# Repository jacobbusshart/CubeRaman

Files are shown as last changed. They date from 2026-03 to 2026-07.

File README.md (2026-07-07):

# CubeRaman

*3D-Printed Raman Spectrometer*

This project aims to make Raman spectroscopy more accessible, replicable and - in the first place - affordable. It can be used to non-destructively identify chemicals, polymers, pharmaceuticals and minerals in an experimental setting.

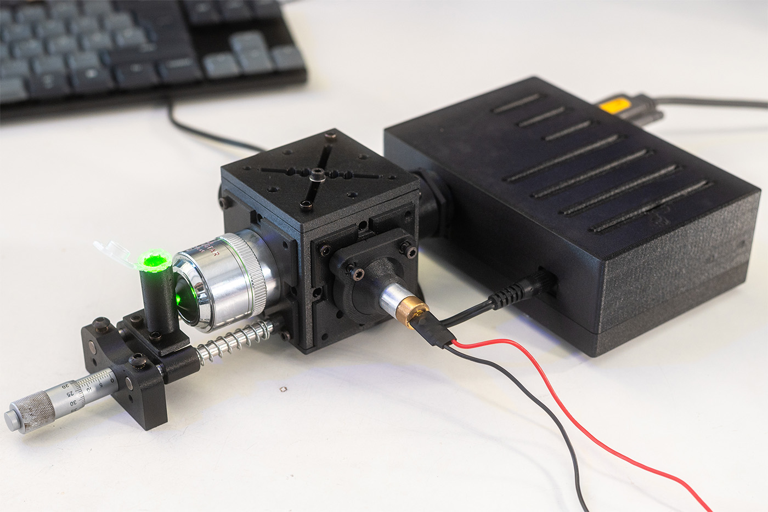
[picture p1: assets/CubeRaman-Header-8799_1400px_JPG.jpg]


It is designed in a back-scattering configuration - both exciting and collecting through the microscope objective. It uses a 532nm laser at ~30mW, utilizing filters with a cut-on at 550nm, which effectively allows for Raman measurements in the wavenumber range of 600cm<sup>-1</sup>- 3000cm<sup>-1</sup>

> ⚠ **This build uses a Class 3B laser. Certified laser safety glasses rated for 532nm are mandatory** — see the note in [Sourced Parts](#sourced-parts). Keep the laser disconnected during assembly and never look into the beam path or the objective, even with protection on. Remove watches and rings while aligning - stray reflections mostly come as a surprise. Know your local regulations for Class 3B laser operation.

**Contents:** [Sample Spectra](#sample-spectra) · [How It Works](#how-it-works) · [3D-Model](#3d-model) · [Sourced Parts](#sourced-parts) · [3D-Printed Parts](#3d-printed-parts) · [Instructions](#instructions) · [Calibration, Alignment & First Light](#calibration-alignment--first-light) · [Software](#software) · [Build Video](#build-video) · [Various](#various)

---
## Sample Spectra
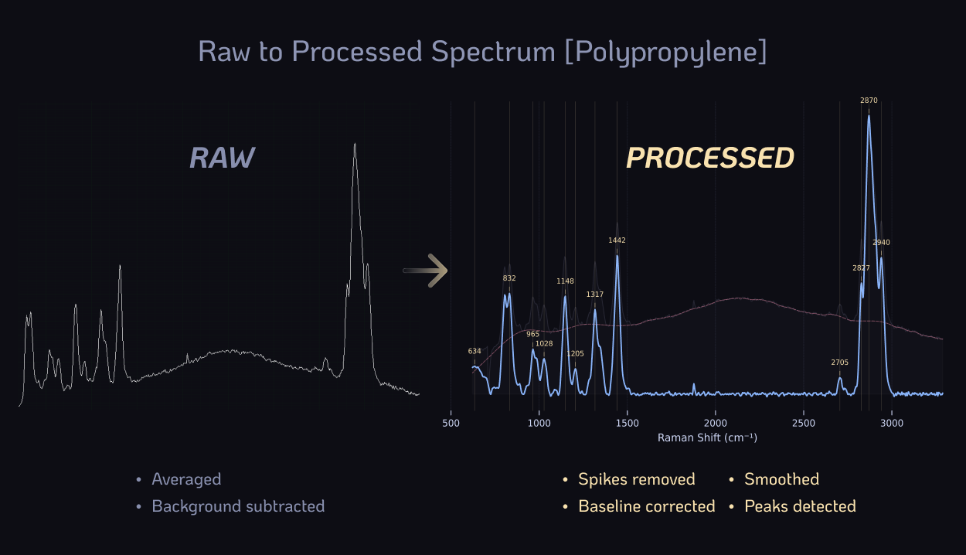
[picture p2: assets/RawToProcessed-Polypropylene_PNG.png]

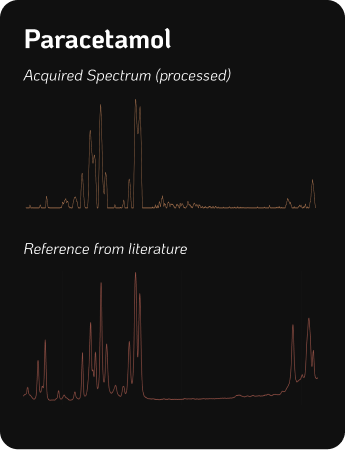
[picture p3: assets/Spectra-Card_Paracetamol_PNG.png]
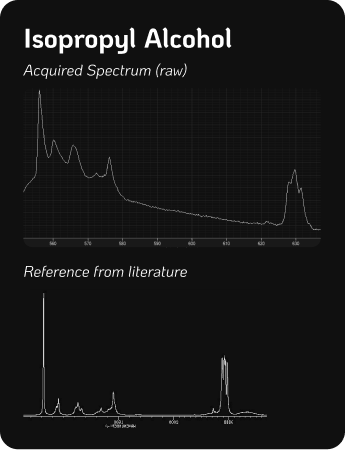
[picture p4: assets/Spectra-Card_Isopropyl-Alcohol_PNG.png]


Verified so far: **polypropylene/-ethylene, paracetamol, isopropyl alcohol, ethanol, diamond, beta-carotene and more.**

Examples of the expected spectral performance. The resolution - how narrow or wide a peak is and thus their separability - is determined by a multitude of factors. With the main bottleneck of the system being the 100 micron input slit of the spectrometer unit. The beam diameter is also a factor, along with its stability and IR-leakage. A higher resolution spectrometer will definitely yield significantly better results - though at a significant cost.

---

## How It Works

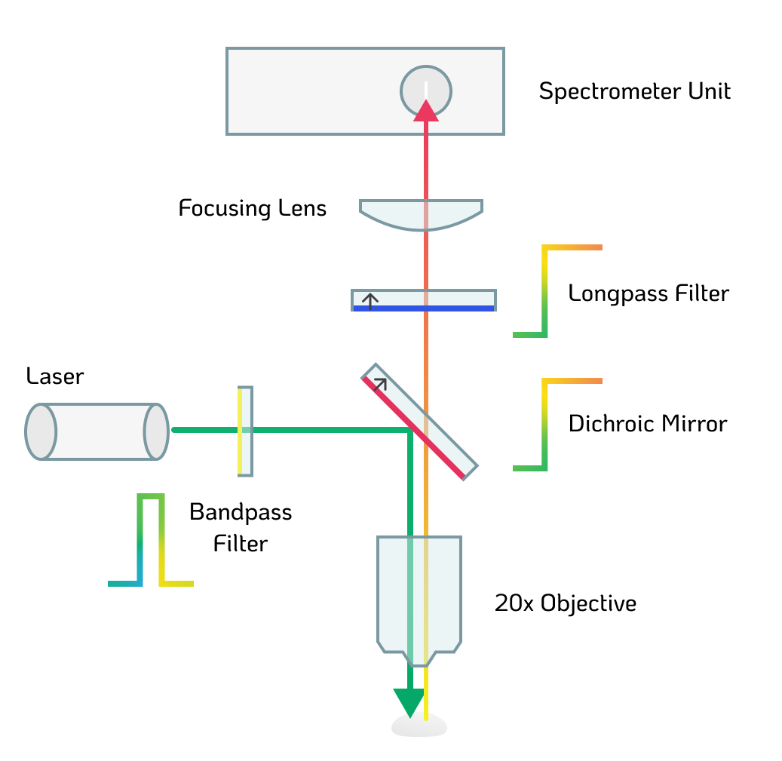
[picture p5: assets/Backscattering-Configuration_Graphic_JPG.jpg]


The **532 nm laser** fires horizontally. The **bandpass filter** strips IR leakage from the cheap diode module and narrows the laser's wavelength. The beam then hits the **DMLP550 dichroic mirror** at 45°, which reflects it 90° downward through the **20x objective** and onto the **sample**.
Backscattered light travels back up through the objective. The Raman-shifted photons (>550 nm) transmit straight through the dichroic toward the detector, while the unwanted Rayleigh-scattered 532 nm light passes into the beam dump. The **FELH0550 longpass filter** gives a second stage of Rayleigh rejection, the **f=19mm achromat** focuses the beam onto the 100 μm slit, and the **B&W Tek spectrometer** records the spectrum.

The acquired spectrum is processed to remove residual background or fluorescence interference and make it more legible. That means: cropping and calculating Raman-shift, cosmic spike removal, baseline correction, smoothing and normalizing. Additionally, peaks can be detected and fitted, though this is more relevant for high-performance/-resolution Raman instruments that have been calibrated to certified standards. See [Software](#software) for the included processing tool.

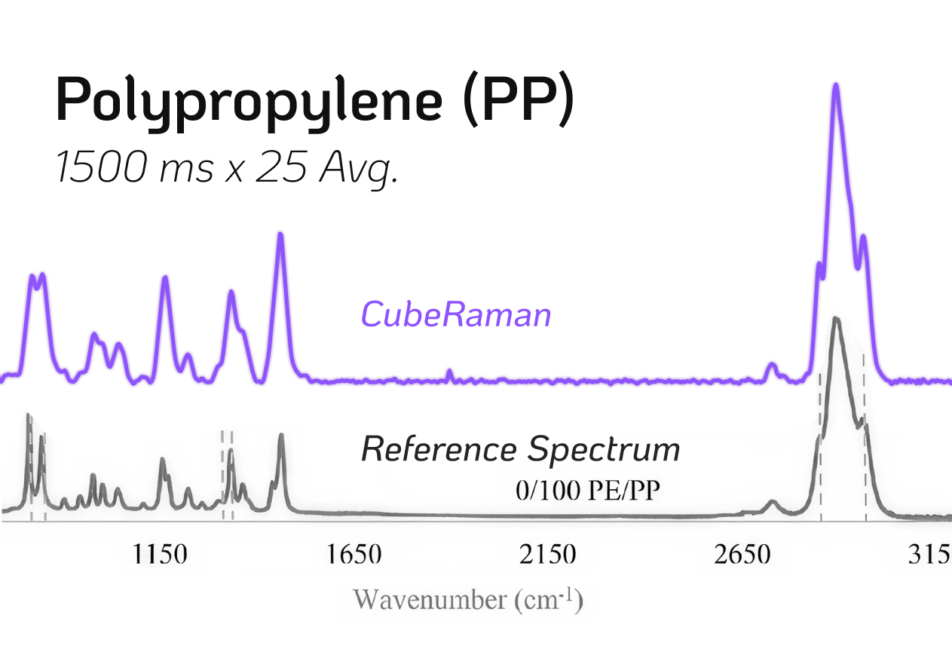
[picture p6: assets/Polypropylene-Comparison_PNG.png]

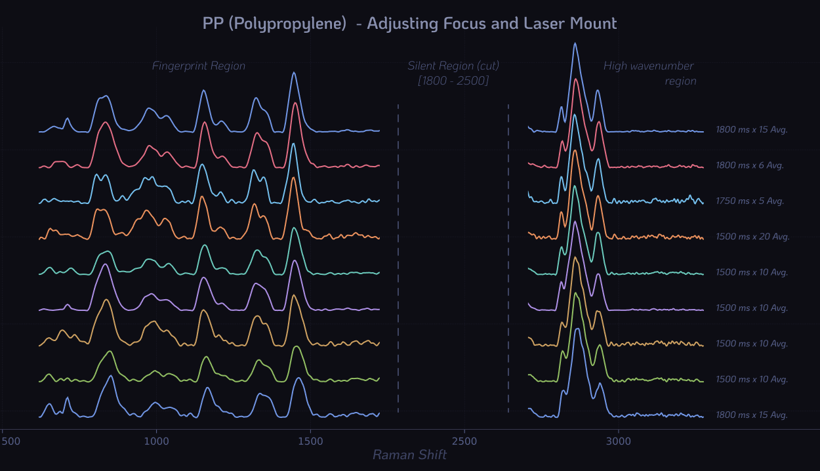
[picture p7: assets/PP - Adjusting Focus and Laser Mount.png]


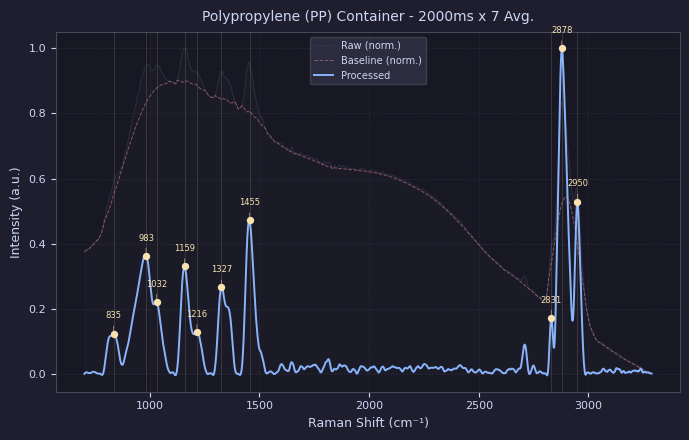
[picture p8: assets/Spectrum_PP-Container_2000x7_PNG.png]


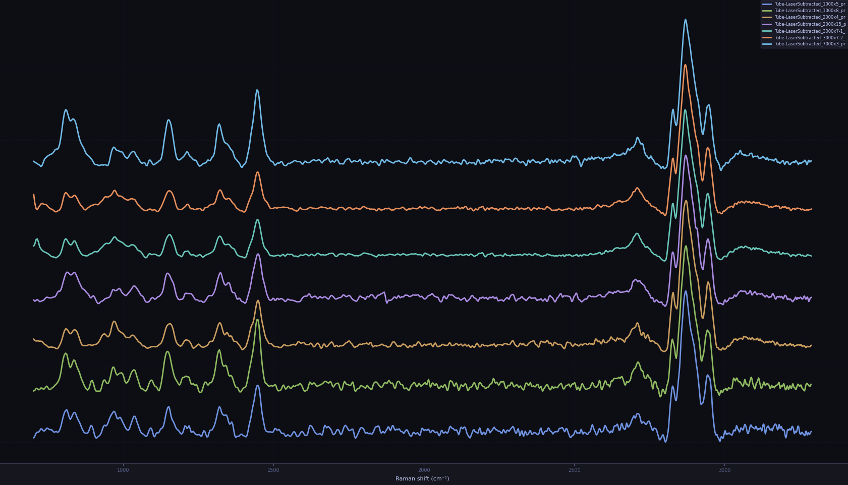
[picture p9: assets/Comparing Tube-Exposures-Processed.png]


--- 

## 3D-Model

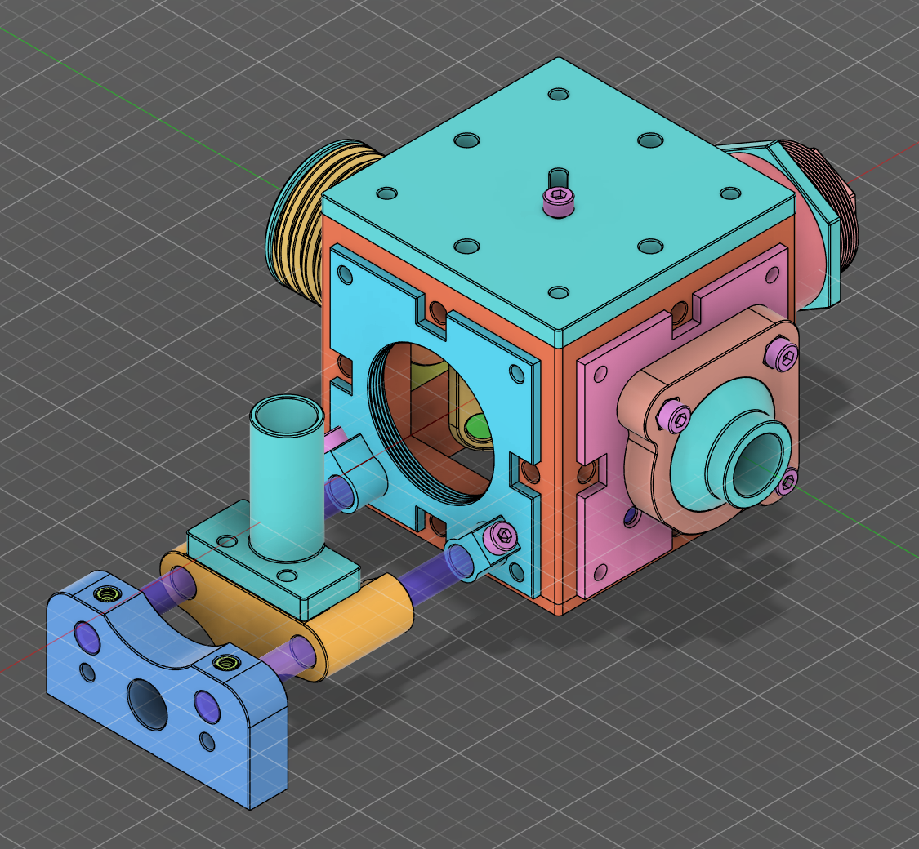
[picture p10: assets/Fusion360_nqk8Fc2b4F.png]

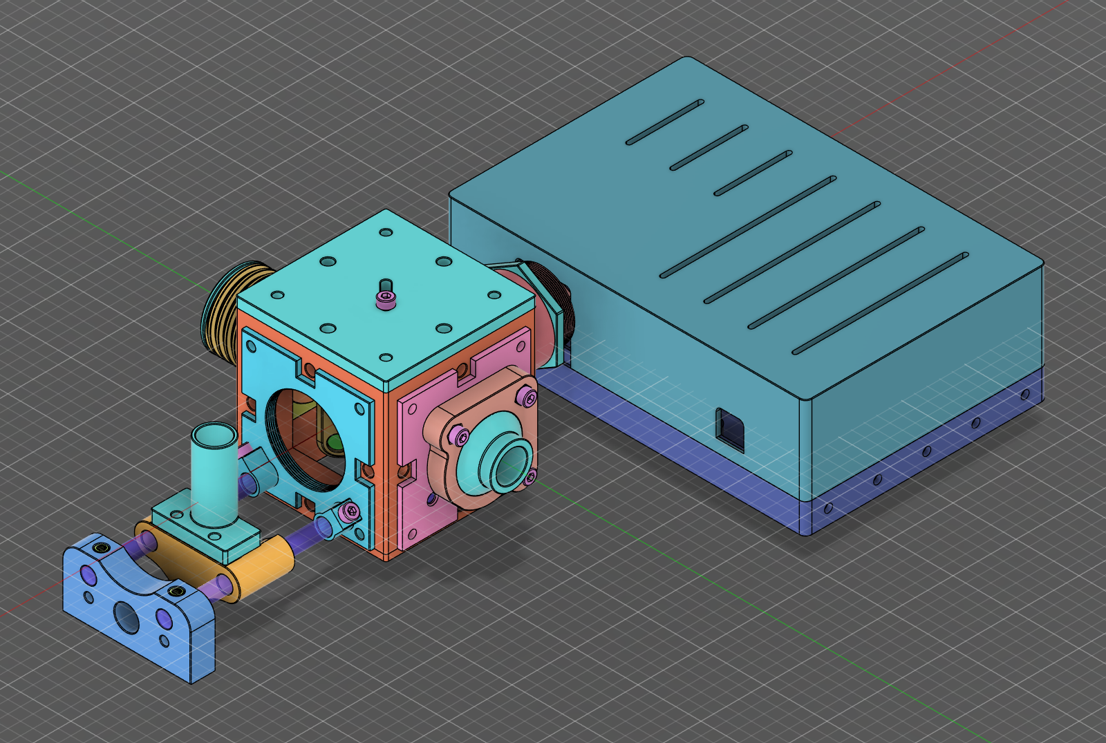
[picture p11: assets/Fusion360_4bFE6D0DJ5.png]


A more detailed overview of the printed parts are depicted in the section below.

---

## Sourced Parts

| Part                                                                                       | Description / Specification                                                                                                                            | Cost                          |
| ------------------------------------------------------------------------------------------ | ------------------------------------------------------------------------------------------------------------------------------------------------------ | ----------------------------- |
| [DMLP550](https://www.thorlabs.com/item/DMLP550)                                           | Ø1" Longpass Dichroic Mirror, 550nm Cut-On                                                                                                             | <p align="right">195€</p>     |
| [FELH0550](https://www.thorlabs.com/item/FELH0550)                                         | Ø25.0mm Longpass Filter, 550nm Cut-On<br>(or the new 1/2" version FELH05550)                                                                           | <p align="right">150€</p>     |
| [#65640](https://www.edmundoptics.com/p/532nm-cwl-10nm-fwhm-125mm-mounted-diameter/20158/) | Bandpass Filter 532nm, 10nm FWHM                                                                                                                       | <p align="right">95€</p>      |
| [AC127-019-A](https://www.thorlabs.com/item/AC127-019-A)                                   | Ø1/2" Achromatic Doublet, f=19mm                                                                                                                       | <p align="right">59€</p>      |
| Microscope Objective                                                                       | Any used/new, infinity-corrected, 20x                                                                                                                  | <p align="right">50€</p>      |
| [B&W Tek BTC 100-2S](https://ebay.us/m/y6hDoC)                                             | Surplus spectrometer unit, 100μm slit, 450-650nm                                                                                                       | <p align="right">180€</p>     |
|                                                                                            | + Any [5V / 2A+ DC Power Supply](https://amzn.eu/d/00yvyamx) (Barrel Jack)<br>+ Any [RS232-to-USB Cable](https://amzn.eu/d/01SqgRPR) for Communication |                               |
| [532nm Laser Pointer](https://aliexpress.com/item/1005004415839015.html)                   | Any (cheap) 532nm laser module, >30mW, (Ø12mm)                                                                                                         | <p align="right">10€</p>      |
| + Various                                                                                  | M3 Screws + Nuts, M3 Heat Set Inserts, <br>Magnets 6x2mm                                                                                               | <p align="right">10€</p>      |
| [Optional](https://aliexpress.com/item/1005008245139319.html)                              | Any Fiber Optic Cable, SMA905, +-200μm core                                                                                                            | <p align="right">(50€)</p>    |
|                                                                                            | <p align="right">**TOTAL**</p>                                                                                                                         | <p align="right">**749€**</p> |

**<u>High-quality laser safety glasses are mandatory to protect your eyes from the powerful laser and its reflections!</u>** Buy a certified pair from a reputable supplier, not Aliexpress! They should be rated for the laser's wavelength at 532nm. I bought [these](https://protect-laserschutz.de/de/shop/~p1924) from a local German brand for around 130€.

Notes on the two "wildcard" parts:
- **Spectrometer**: the BTC 100-2S is the cost compromise of this build - its 100μm slit is the main resolution bottleneck. Any spectrometer covering roughly 550-650nm will work; a better one yields sharper peaks, though often at significant cost.
- **Microscope Objective**: must be **infinity-corrected** - the design places the dichroic and longpass filter in collimated space and uses the achromat as the tube lens. A finite (160mm) objective will not work without redesign! Also keep in mind that anything >20x often features a working distance too short for measuring inside containers or a cuvette (though at higher NA = more signal). 20x is the best compromise, from my experience at least.

---
## 3D-Printed Parts

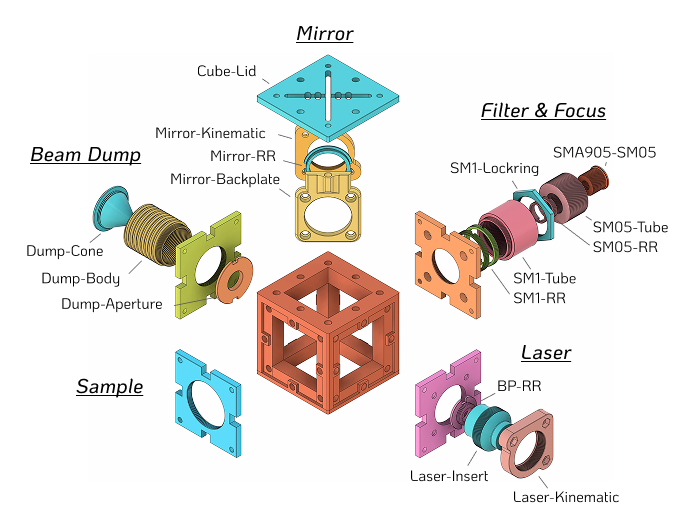
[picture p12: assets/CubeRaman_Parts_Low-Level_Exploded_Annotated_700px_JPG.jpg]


### Base Cube & Sides

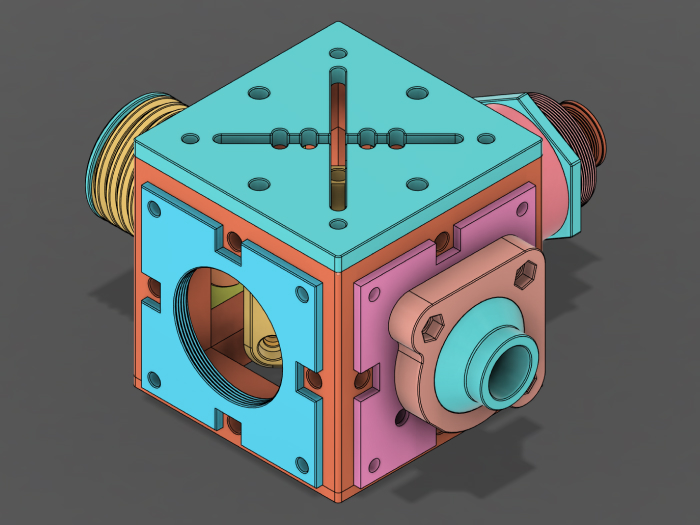
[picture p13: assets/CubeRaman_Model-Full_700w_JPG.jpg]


Print the base cube along with the side plates first. Afterwards print the rest of the grouped parts below.

All parts were printed without supports and are only printed once!

| Base Cube + Sides       |
| ----------------------- |
| Base-Cube               |
| Base-Cube-Top           |
| Cube-Insert_Sample      |
| Cube-Insert_Dump        |
| Cube-Insert_Laser       |
| Cube-Insert_FilterFocus |

### Parts

| **Laser**       | **Mirror**       | **Filter & Focus** | **Beam Dump** | **Sample** |
| --------------- | ---------------- | ------------------ | ------------- | ---------- |
| Laser-Insert    | Mirror-Kinematic | SM1-Tube           | Dump-Body     | -          |
| Laser-Kinematic | Mirror-Backplate | SM05-Tube          | Dump-Cone     |            |
| BP-RR           | Cube-Lid         | SM1-Lockring       | Dump-Aperture |            |
|                 | Mirror-RR        | SMA905-SM05        |               |            |
|                 |                  | SM1-RR (2x)        |               |            |
|                 |                  | SM05-RR (2x)       |               |            |

| **Extras**     |
| -------------- |
| Spanner_SM1RR  |
| Spanner_SM05RR |

Printed on a Bambu P1S using high resolution exports out of Fusion and sliced using BambuStudio

- PETG-CF (Black) 
- 0.4mm Hardened Steel Nozzle
- 0.12mm Layer height
- 4 Walls, 50% Gyroid infill
- Seam position Nearest or Random
- Precision parameters set to 0.001mm

---
## Instructions

*Full step-by-step version: [Hackaday.io Instructions](https://hackaday.io/project/205344/instructions)*

- I use a Bambu P1S with a 0.4mm hardened steel nozzle and extruder
- Filament is ideally non-reflective and dark / black to reduce stray light; I used black PETG-CF as it's my favorite and matte. The stiffer the better; PLA-CF is also a sensible alternative. 
### 1. Printing

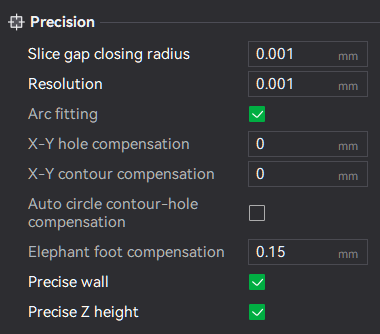
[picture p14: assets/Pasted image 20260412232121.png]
- Set "**Precision**" settings in your slicer (*may just be placebo*) 
- **No Supports** are needed for any of the parts!
- **Print Orientation**: face flat / perpendicular to the build plate - especially for threads, which must be printed vertically for clean engagement! "**Auto-Orient**" should always do the trick.
- **Layer Height** set to at least **0.12mm**. (at least for the parts with threads or fine features) 
- "**Seam Position**" is set to **Nearest** or Random for a better fit.

- All parts should be easy to print; the Base-Cube being the most demanding, as it features overhangs. (TO BE REVISED to 45° to facilitate printing)
- For the **Cube-Inserts** and the **Cube-Lid** especially, it is best to let the build plate / part cool down before removing it. This is good practice to avoid bending the part and introducing permanent deformation.
- Also print the two spanner tools (**Spanner_SM1RR**, **Spanner_SM05RR**) - they make tightening the retaining rings much easier later.

### 2. Assembly

#### Base-Cube

**Printed Parts:** Base-Cube, Base-Cube-Top
**Sourced Parts:** (24x) M3 Heat Set Inserts (Length: 4mm, Outer Diameter: 4mm), (24x) M3 x 8mm Screws

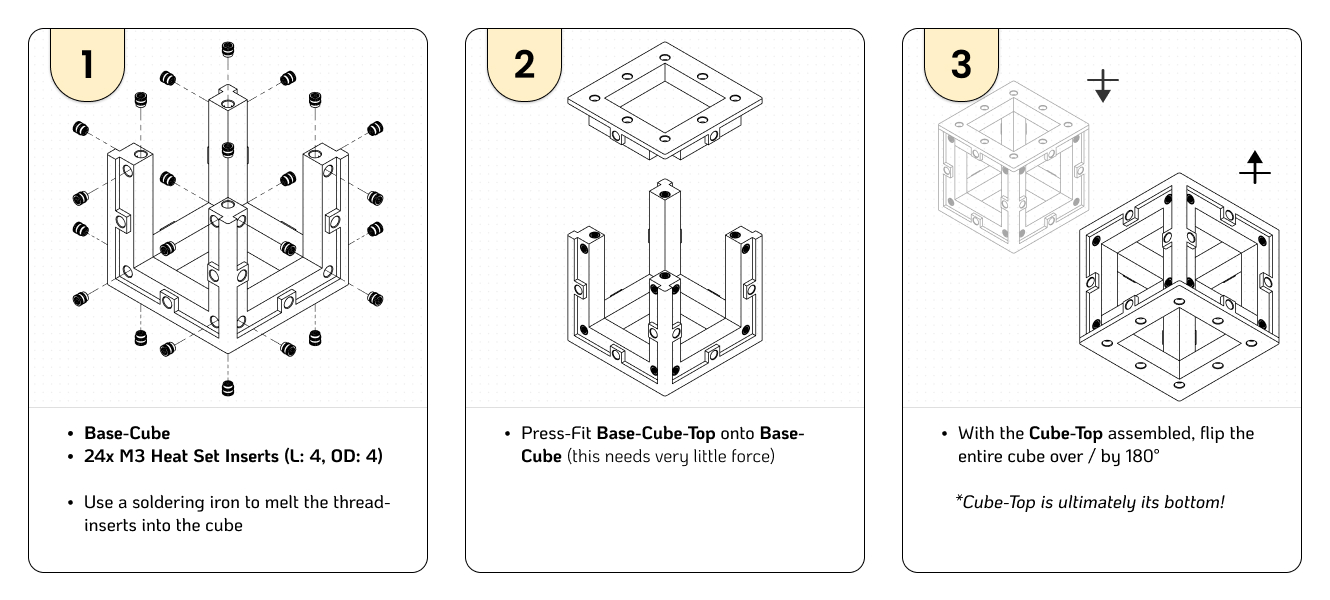
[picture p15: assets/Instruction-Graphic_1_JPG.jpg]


1. Melt the heat-set inserts into the bosses of the Base-Cube using a soldering iron. Keep the iron perpendicular and let the plastic - not force - do the work.
2. Fasten Base-Cube-Top with M3 x 8mm screws.

Note: You don't have to insert all the threads at first. I initially didn't put any on the bottom (of Step 1 in the graphic) and on one side, which later contains the Beam Dump and was simultaneously used as an opening to get to the adjustment screws of the 45° mirror inside. The clearances of the Cube-Inserts are relatively tight - even more, if the overhangs on the cube sag a little. In the testing stages I mostly used 2 screws (top-left and bottom-right) for each of the other Cube-Inserts (Laser, Sample, FilterFocus).  

**Now that the Base-Cube is set up you can start putting together the Cube-Insert sub-assemblies. The following sections *don't* need to be performed in order.** 


*Parts might have been slightly modified, assume this to be an outdated overview*

#### Laser

**Printed Parts:** Cube-Insert_Laser, Laser-Kinematic, Laser-Insert, BP-RR (only if Bandpass Filter is used)
**Sourced Parts:** 532nm Laser (Ø12mm), Recommended but optional: [Bandpass Filter #65640](https://www.edmundoptics.com/p/532nm-cwl-10nm-fwhm-125mm-mounted-diameter/20158/), 4x Magnets (Ø6mm, width: 2mm), 3x M3 x 8mm Screws + Nuts (Fine-Pitch .35 Screws / Nuts are preferred but normal also work)

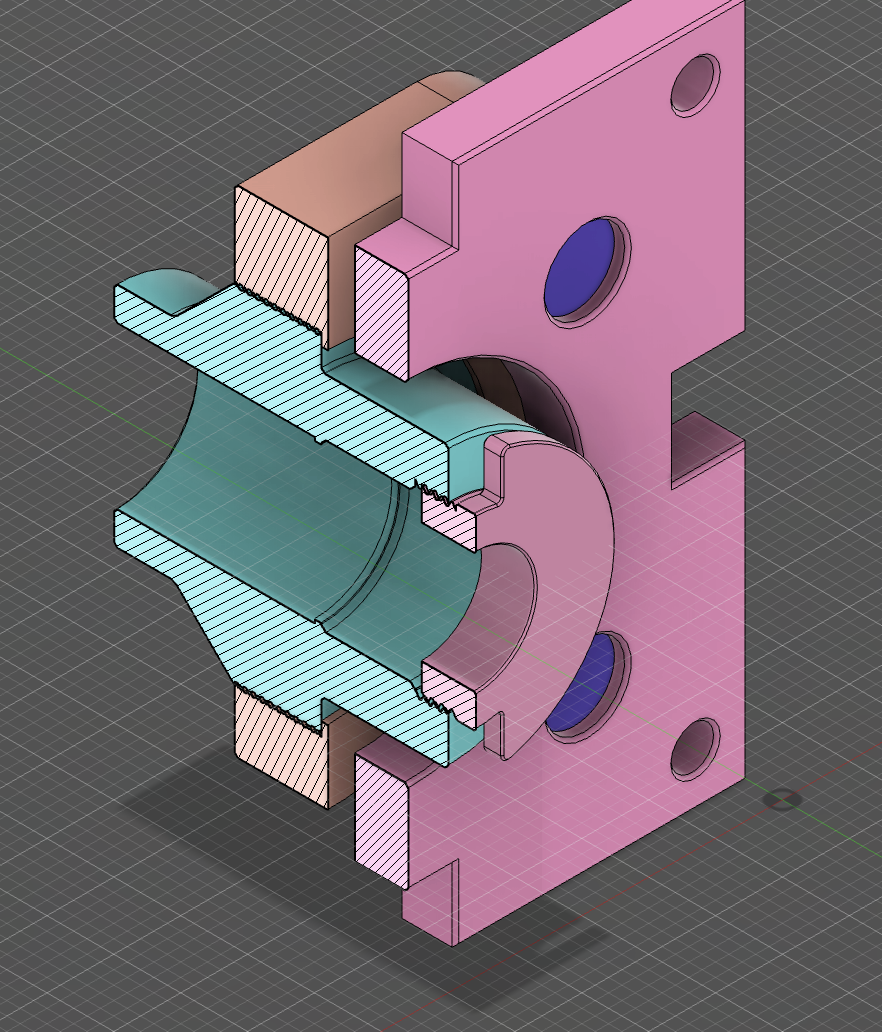
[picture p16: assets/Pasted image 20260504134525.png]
 
*Laser and Bandpass Filter are not depicted in the graphic*

1. Press the *Magnets* into the openings on *Cube-Insert_Laser*. 
	1. Since the respective mating part - *Laser-Kinematic* - features 3 screws, you can also insert just 3 magnets. Though keep in mind that this will allow more stray light to enter the cube. 
2. Now press the *M3 Nuts* into *Laser-Kinematic*.
3. For best results use a hammer on the screw head while inserted to ensure the nuts are flush and inserted all the way.
	1. If you want them permanently fixed, you may use a soldering iron to lightly melt the nuts in. This isn't necessary with current sufficiently tight clearances.
4. The *Laser* module is friction press-fit into *Laser-Insert*. Ensure the Laser's front surface sits perpendicularly flush.
5. Now press the *Bandpass Filter* into the other side of *Laser-Insert*.
	1. The orientation is important as both sides feature different coatings: the purple side should face you (so you see purple when assembled). 
	2. KEEP LASER DISCONNECTED AND NEVER LOOK DIRECTLY INTO THE LASER, EVEN WHEN WEARING LASER-PROTECTION!
6. It should already sit tight, but in addition *BP-RR* is lightly screwed on until it secures the rim of the filter.
7. Finally screw the assembled *Laser-Insert* into the printed thread of *Laser-Kinematic*.
8. With the entire laser and filter assembly now sitting on *Cube-Insert_Laser*, it can be pressed into a side of *Base-Cube* and fastened with 4 screws.

**Powering the Laser:** The module is specced for 3.7V, but I run it at **2.7-3.0V** from a bench supply via its two bare leads (or via a voltage regulator from a powerbank now). Higher voltage doesn't buy a cleaner beam - just more heat (I'm not using the heatsink yet, as my magnets are too weak to carry the added weight) and more noise. The lower range has been the better operating point in my measurements.

#### Sample

**Printed Parts:** Cube-Insert_Sample
**Sourced Parts:** Microscope Objective (20x, Infinity-Corrected, M32-Thread)

1. Make sure the *Microscope Objective* thread matches the printed part (currently only M32 and M25 available, contact me at Jacob@Busshart.de for variations)
2. With the *Microscope Objective* positioned perpendicular on the thread, carefully thread it into *Cube-Insert_Sample*. This may require more force initially, especially the first time. 
3. When the *Microscope Objective* sits flush with the surface of *Cube-Insert_Sample*, the assembly can be pressed into the side to the left of *Cube-Insert_Laser* (or as depicted in the graphic) and fastened with 4 screws.

Note on working distance: the objective's working distance decides what you can measure through container walls. Mine is 2.4mm - enough to measure ethanol *through* a plastic bottle wall (see [Various](#various)).

*MORE FOR THE FULL MICROMETER ASSEMBLY / FOCUS STAGE COMING SOON*

#### Dichroic Mirror

**Printed Parts:** Mirror-Kinematic, Mirror-Backplate, Mirror-RR, Cube-Lid
**Sourced Parts:** DMLP550, 3x M3 Screws + Nuts, Magnets (Ø6mm, width: 2mm)

*Be mindful of the orientation of both the **FELH0550** and the **DMLP550** as they have to be installed in the correct orientation. Make sure the direction on the rim of both optics corresponds with the arrows in the graphic below:*


1. Seat the *DMLP550* in the 45° pocket of *Mirror-Kinematic* and secure it with *Mirror-RR*. Handle the dichroic by its edges only - fingerprints on the coating directly cost signal.
2. Press the *M3 Nuts* and *Magnets* into *Mirror-Backplate* / *Mirror-Kinematic* analogous to the Laser assembly: the magnets preload the mirror platform against the 3 adjustment screws, providing tip/tilt.
3. Lower the assembly into *Base-Cube* and close the top with *Cube-Lid*.
4. The adjustment screws remain reachable through the (still open) Beam Dump side of the cube for alignment.

#### Beam Dump

**Printed Parts:** Cube-Insert_Dump, Dump-Body, Dump-Cone, Dump-Aperture
**Sourced Parts:** -

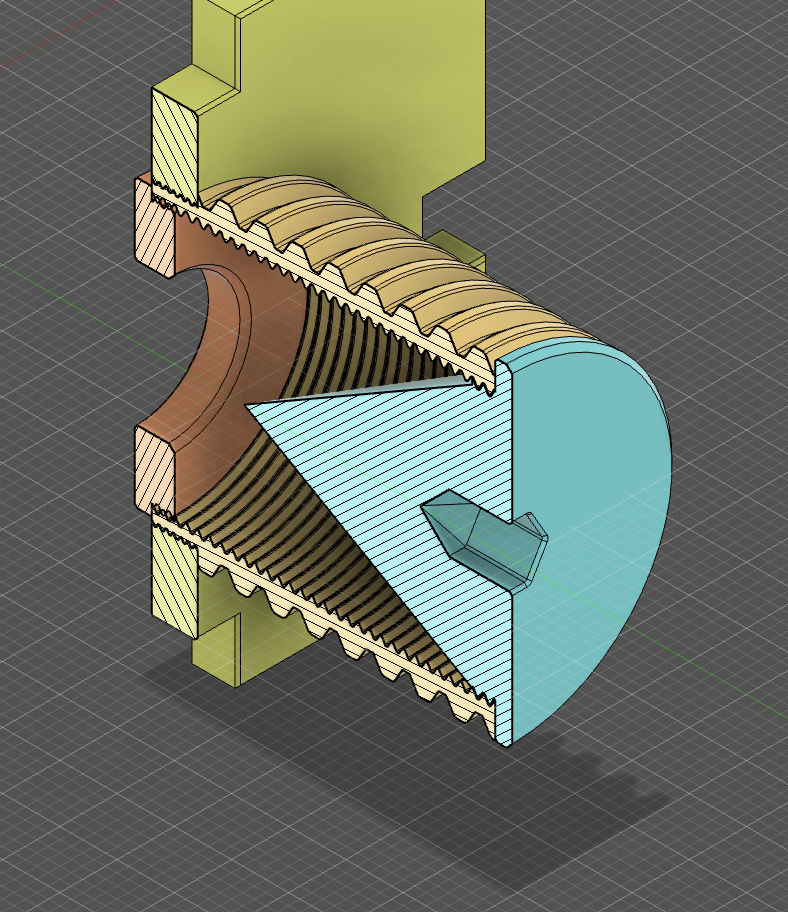
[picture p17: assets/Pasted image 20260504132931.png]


1. Screw the printed parts together.
2. *Dump-Body* being the main part, which is screwed into *Cube-Insert_Dump*. 
3. Screw on the *Dump-Cone* to create a light-sealed cavity.
4. *Dump-Aperture* is screwed on from the opposite side or as depicted in the graphic.
	1. This aperture is not strictly necessary but could improve light suppression.

The dump sits opposite the laser: the laser light that transmits straight through the dichroic (plus Rayleigh-scattered 532nm returning from the sample) ends up trapped here instead of bouncing around the cube. The Beam Dump as a whole was designed to be as modular as possible to allow for different cone angles and aperture sizes to be tested and interchanged.

**Tip:** Leave this insert unfastened until alignment is finished - its opening is your access port to the mirror adjustment screws.

#### Filter & Focus

**Printed Parts:** Cube-Insert_FilterFocus, SM1-Tube, SM05-Tube, SM1-Lockring, SMA905-SM05, (2x) SM1-RR, (2x) SM05-RR + Spanner_SM1RR, Spanner_SM05RR
**Sourced Parts:** FELH0550 Longpass Filter, AC127-019-A Achromatic Doublet, B&W Tek BTC 100-2S

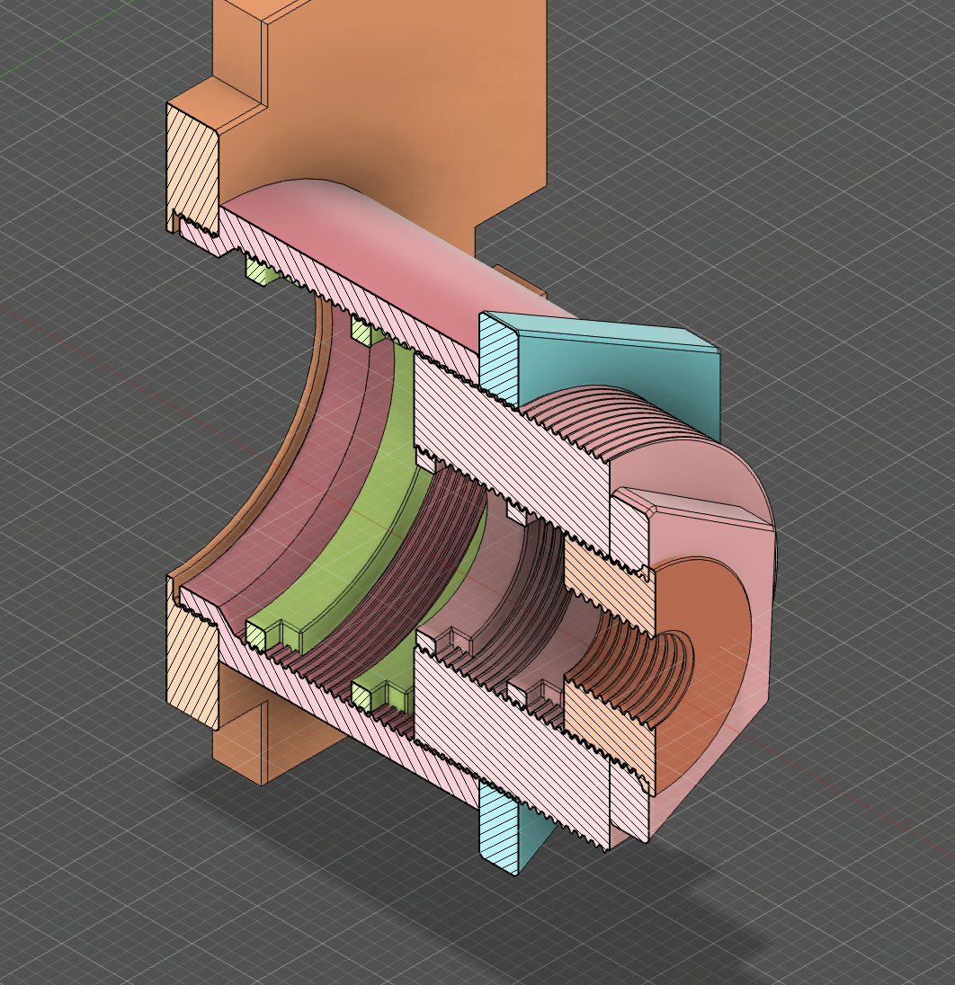
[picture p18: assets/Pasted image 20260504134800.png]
 
*Longpass Filter, Focusing Lens and Spectrometer unit are not depicted in the graphic*

This is the detection arm: collimated Raman light exits the dichroic, gets a second stage of Rayleigh rejection from the longpass filter, and is focused by the achromat onto the spectrometer's 100μm slit.

*Be mindful of the orientation of the **FELH0550** - make sure the direction on the rim corresponds with the arrows in the orientation graphic above.*

1. Thread one *SM1-RR* into *SM1-Tube* as the lower seat - it determines the axial position of the filter.
2. Drop in the *FELH0550* and clamp it flat with the second *SM1-RR* from above.
	1. The printed rings are only 2-2.5mm thick and somewhat flexible: thread them in with **pure rotation, no downward force**, keeping them as perpendicular as possible so the filter sits truly square.
	2. Use the printed *Spanner_SM1RR* - it engages the two openings of the ring and prevents it from going in crooked.
3. Mount the *Achromatic Doublet* into *SM05-Tube* between the two *SM05-RR*, same technique (use *Spanner_SM05RR*).
	1. **Orientation matters:** the more strongly curved surface faces the collimated beam (toward the cube), not the focused end - check this when removing the lens from its shipping mount.
4. Thread *SM05-Tube* into *SM1-Tube*. Their relative thread position is the **focus adjustment** onto the slit.
5. Couple to the spectrometer via the *SMA905-SM05* adapter: the output of the lens tube screws directly onto the SMA905 input of the spectrometer. Clean and rigid, no fiber run between optics and detector.
	1. Alternatively, use the optional SMA905 fiber (~200μm core) if the spectrometer should be positioned remotely, though this might require additional adjustment options for efficient coupling.
6. Fasten *Cube-Insert_FilterFocus* into the cube side opposite the Sample port. Once the focus is finalized during alignment you can optionally clamp everything with *SM1-Lockring*.

**Spectrometer hookup:** 5V / 2A+ barrel-jack supply for power, RS232-to-USB cable for communication with the computer. I reuploaded the original **SpectrumStudio** acquisition software [here](https://drive.google.com/file/d/1ooKja8GXg5gMX-swFjbmAXFP61ucyWT_/view?usp=sharing). (Alternatively you can write your own software to communicate with the spectrometer via the serial connection.)

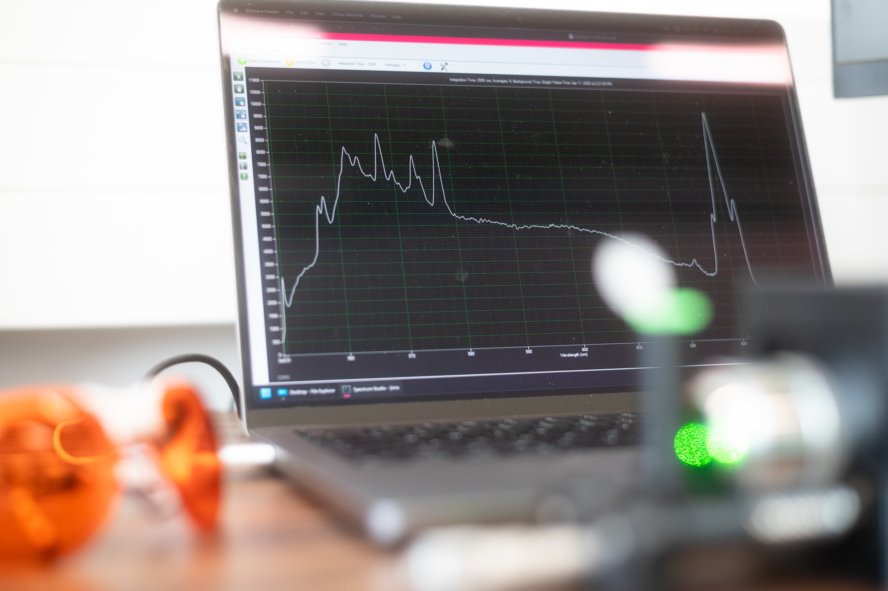
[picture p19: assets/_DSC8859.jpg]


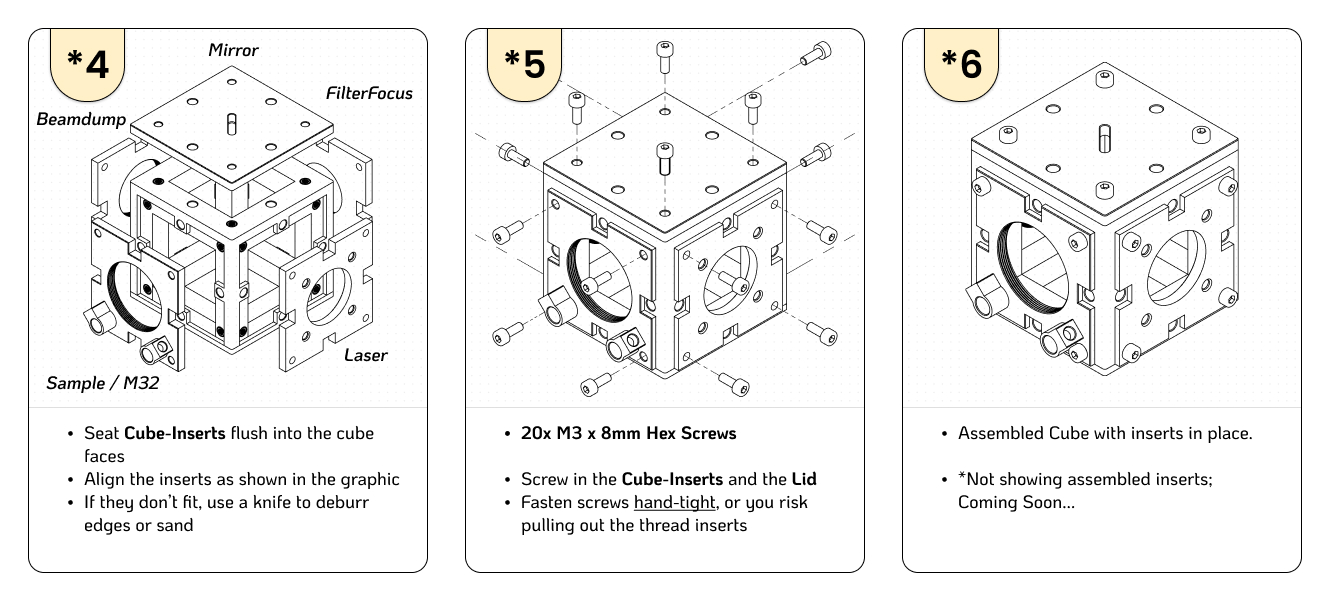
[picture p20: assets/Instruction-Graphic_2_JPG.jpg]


---

## Calibration, Alignment & First Light

**Spectrometer calibration** is an important prerequisite. Use a calibration lamp, any CFL (with a known spectrum) or a mercury vapor lamp: acquire a spectrum of exclusively said lamp in a dark room, note the pixel index of each line in SpectrumStudio and match it with the corresponding reference wavelength from your source. With more than 4 points sampled - ideally as many as you can get - enter them into the table in SpectrumStudio, which automatically calculates the correct calibration coefficients.

⚠ **Glasses on. Room cleared of reflective clutter. Lowest usable laser voltage (~2.7V).**

1. With the Beam Dump insert still off, power the laser and check that the beam hits the dichroic centrally and exits through the objective.
2. Use the laser's kinematic screws (magnet-preloaded tip/tilt) to center the beam on the objective's back aperture; use the mirror's kinematic screws - reached through the dump opening - to make the beam exit the objective straight and centered.
3. Place a strong Raman scatterer with a known spectrum at the focus. Good first samples: **polypropylene** (any PP container), **isopropyl alcohol**, or - if you have one - a **diamond**, whose single sharp line at 1332cm<sup>-1</sup> can be a nice start.
4. Take continuous acquisitions (around 1000ms) while slowly adjusting the SM05/SM1 tube focus and the sample distance until the Raman peaks maximize. Expect this to be iterative between laser tilt, mirror tilt, and focus.
5. Optionally lock the *SM1-Lockring*, install the Beam Dump, and close up the cube.

For liquids in containers: thin-walled vials/cuvettes work best; thick glass mostly returns the silica spectrum of the glass itself (see the working distance note in [Sample](#sample)).

---

## Software

**Acquisition:** [SpectrumStudio](https://drive.google.com/file/d/1ooKja8GXg5gMX-swFjbmAXFP61ucyWT_/view?usp=sharing) (reupload of the original B&W Tek software) via the RS232-to-USB connection - or write your own via the serial protocol.

- Raman-shift conversion (532nm excitation) and cropping to the usable 600-3000cm<sup>-1</sup> window
- Cosmic spike removal (modified Z-score on the derivative)
- Baseline correction: **ALS**, **arPLS** or **SNIP**
- Savitzky-Golay smoothing and normalization
- Pseudo-Voigt peak detection and fitting
- Reference-library matching (peak scoring + cosine similarity) with overlays and CSV export - only if you have a library file, as I unfortunately can't provide that

---

## **Build Video**

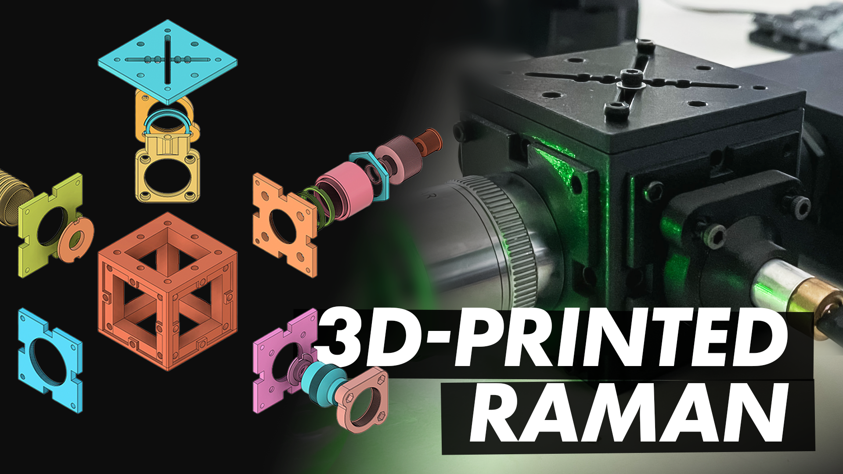
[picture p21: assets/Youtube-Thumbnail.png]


**[Click here to watch the build process! - Youtube](https://youtu.be/bUxc6mWsTgc)**

[Click here to watch the library-matching update! - Youtube](https://www.youtube.com/watch?v=tDqg5P3a8J0)

--- 

## Various

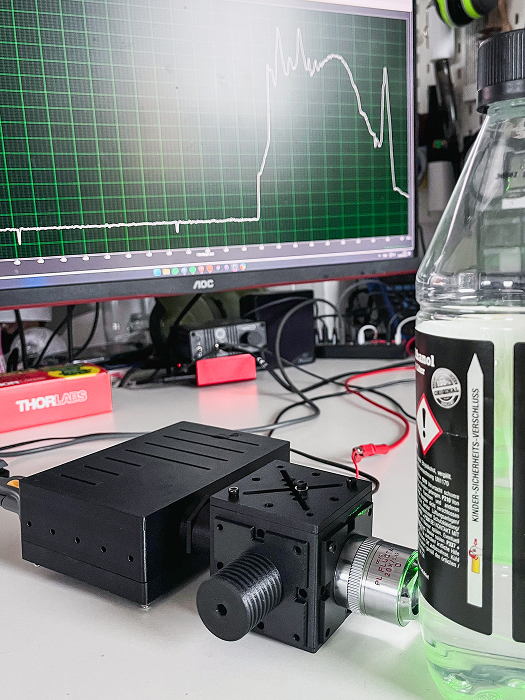
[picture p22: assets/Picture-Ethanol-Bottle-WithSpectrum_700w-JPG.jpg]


Testing capabilities during calibration in full daylight: depending on the focus distance you either detect the Raman spectrum of the bottle content - in this case Ethanol/Water - or the bottle itself. This only works if your microscope objective's working distance is greater than the wall width of the container to be measured. Here the working distance is 2.4mm, which is sufficient.

---

Questions? Jacob@Busshart.de - or comment on the [video](https://youtu.be/bUxc6mWsTgc).

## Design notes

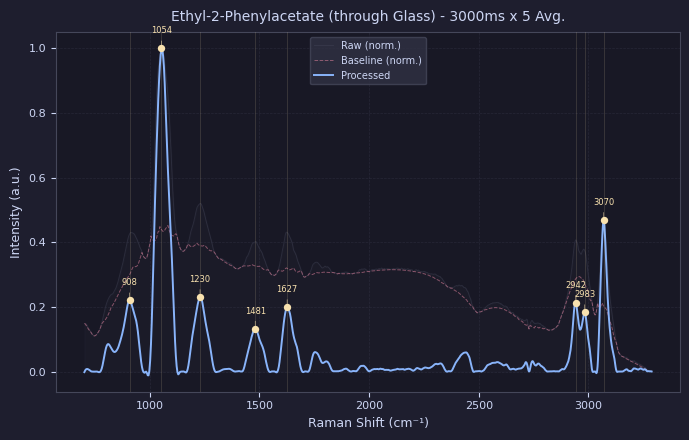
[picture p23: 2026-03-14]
assets/Spectrum_Ethylphenylacetate-ThroughGlass_3000x5_PNG.png

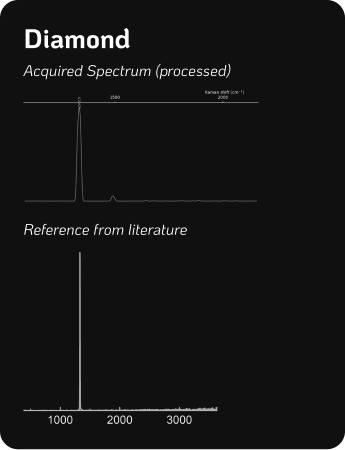
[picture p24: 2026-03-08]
assets/Spectra-Card_Diamond_PNG.png

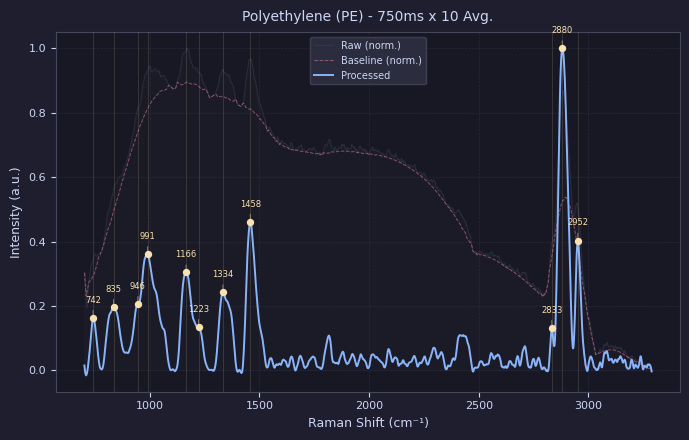
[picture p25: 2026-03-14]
assets/Spectrum_PE-Container_750x10_PNG.png

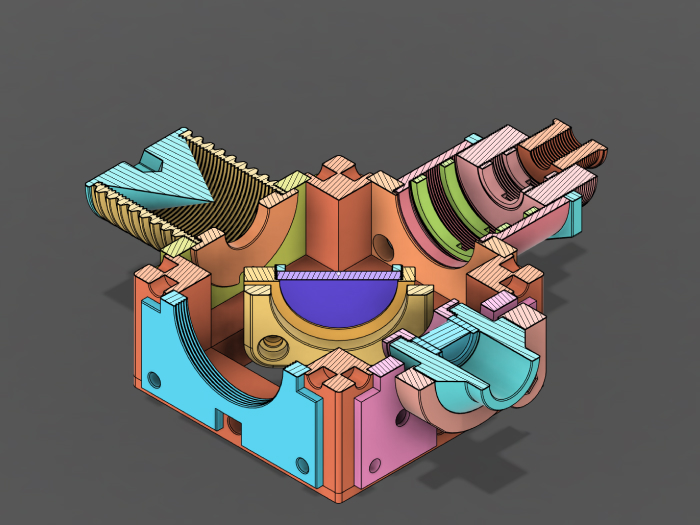
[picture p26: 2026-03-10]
assets/CubeRaman_Model-HalfCut_700w_JPG.jpg

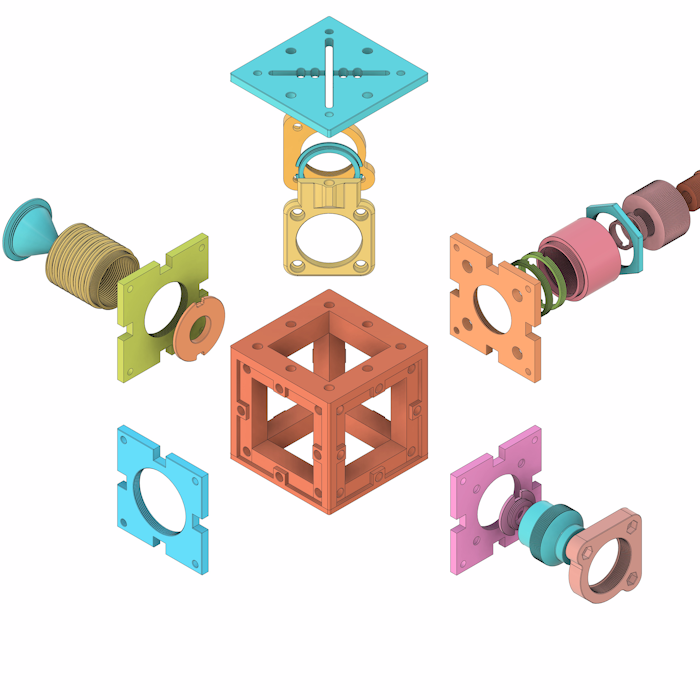
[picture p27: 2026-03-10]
assets/Explode_Low-Level_Still-End.png

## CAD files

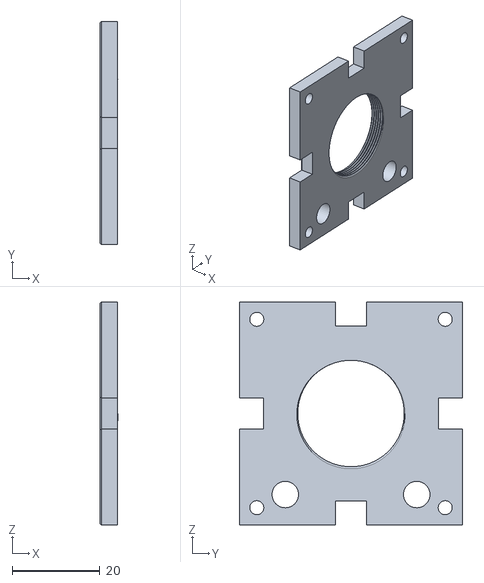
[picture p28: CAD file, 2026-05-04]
parts/Cube-Insert_Sample_M25.stl
4.02 x 50.9 x 50.9

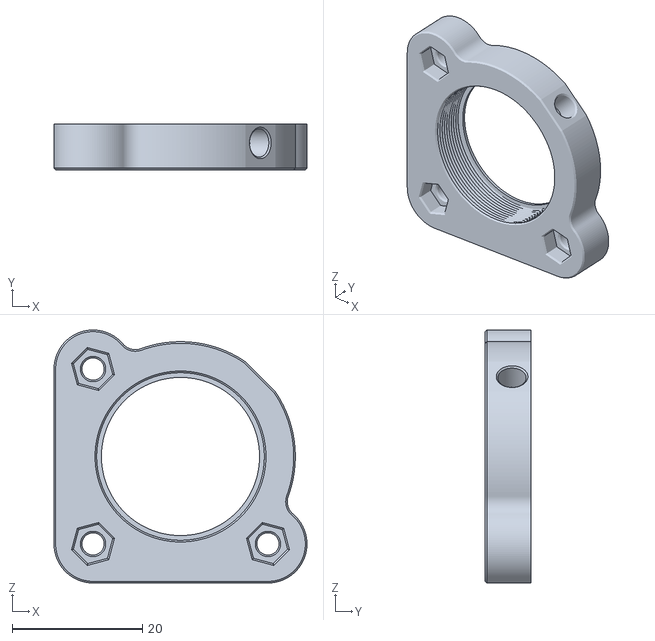
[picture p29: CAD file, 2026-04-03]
parts/Laser-Kinematic.stl
38.9 x 7.00 x 38.9

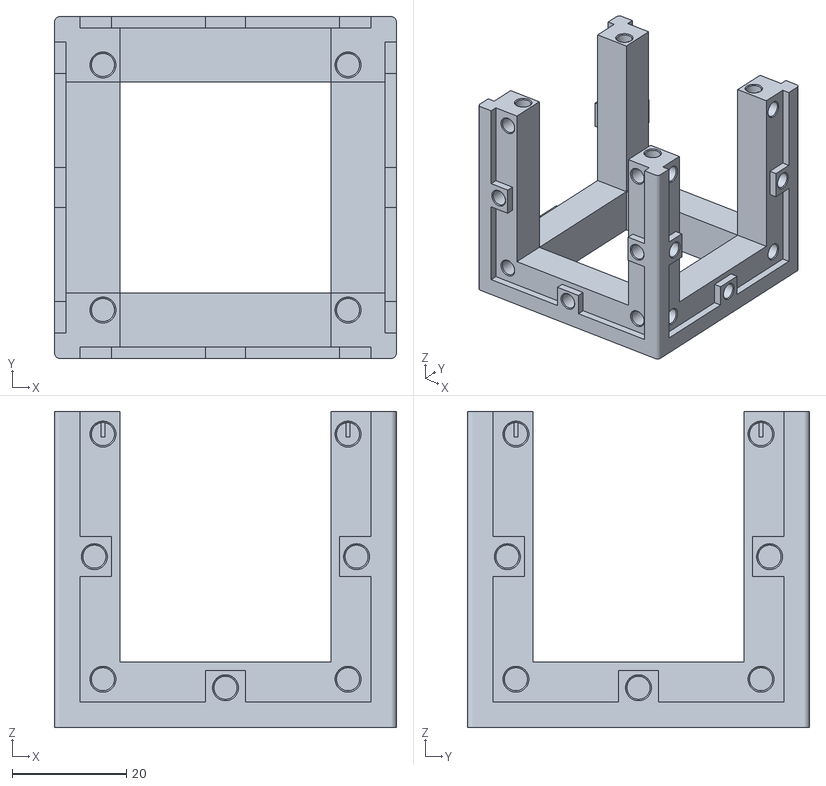
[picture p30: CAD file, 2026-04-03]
parts/Base-Cube.stl
60.0 x 60.0 x 55.5

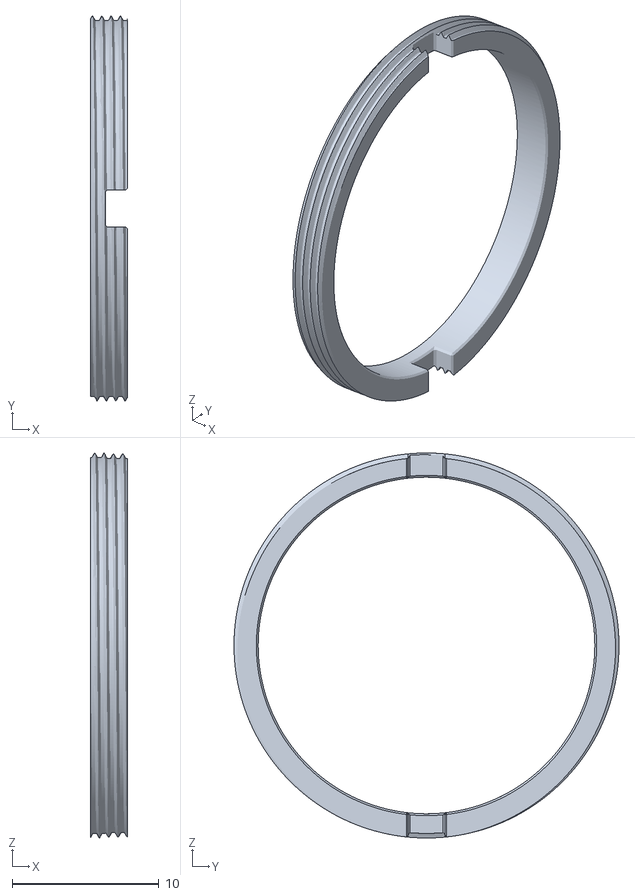
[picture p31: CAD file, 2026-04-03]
parts/SM1-RR-Short.stl
2.51 x 26.2 x 26.2

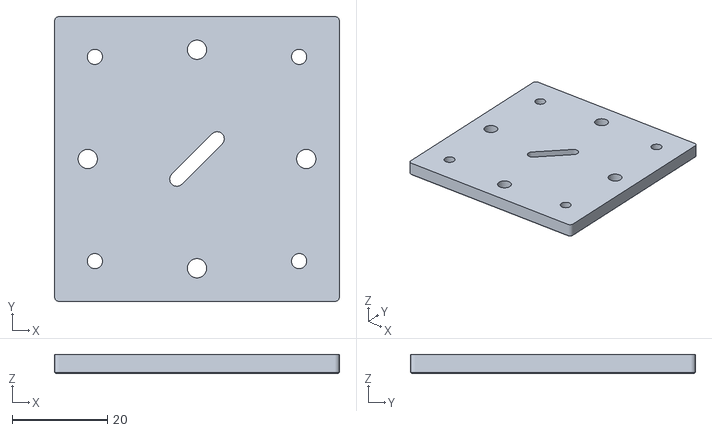
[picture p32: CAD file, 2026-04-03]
parts/Cube-Lid.stl
60.0 x 60.0 x 4.00

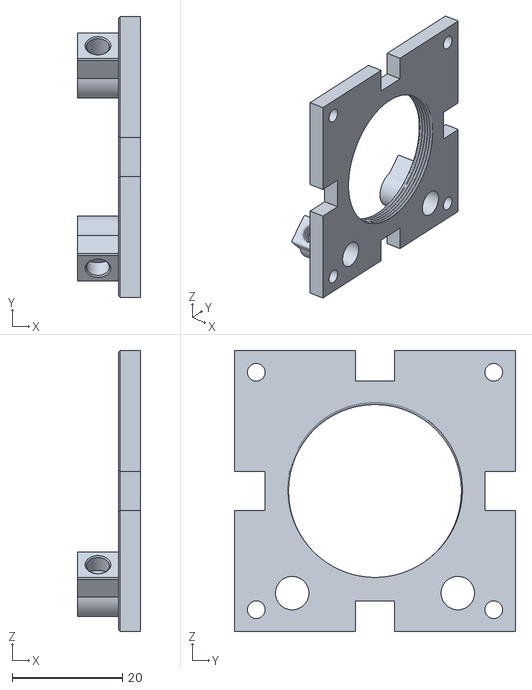
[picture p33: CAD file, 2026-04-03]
parts/Cube-Insert_Sample.stl
11.5 x 50.9 x 50.9

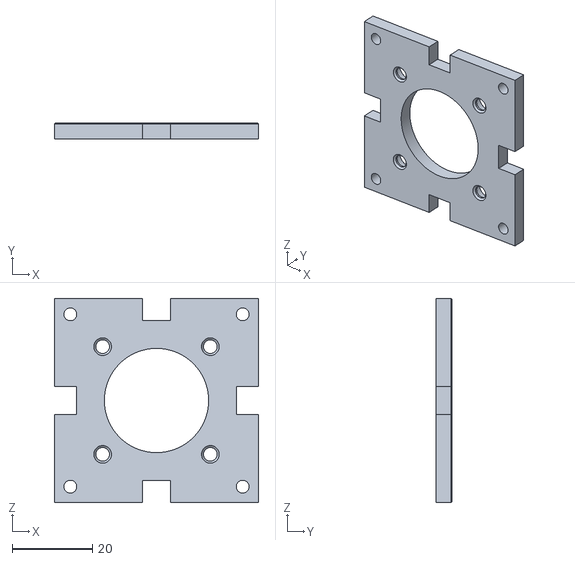
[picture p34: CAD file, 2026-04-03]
parts/Cube-Insert_Laser.stl
50.9 x 4.00 x 50.9

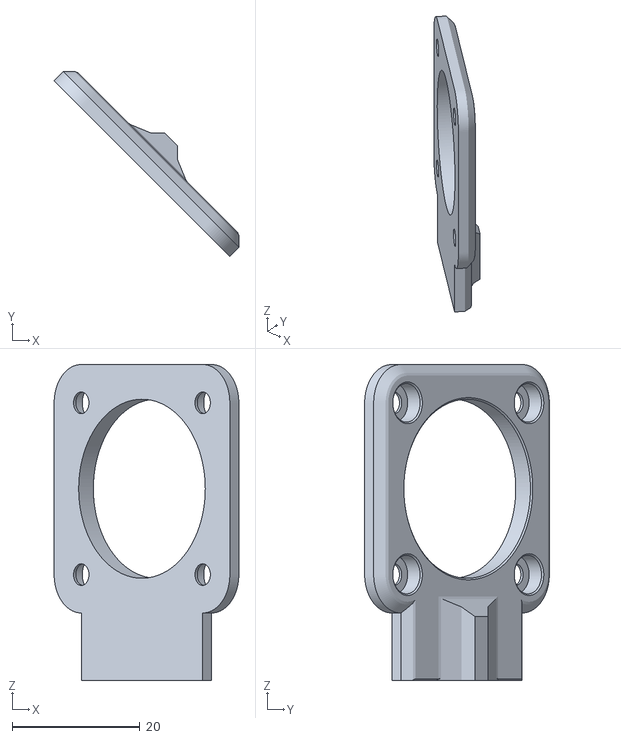
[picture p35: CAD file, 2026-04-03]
parts/Mirror-Backplate.stl
28.9 x 28.9 x 49.4

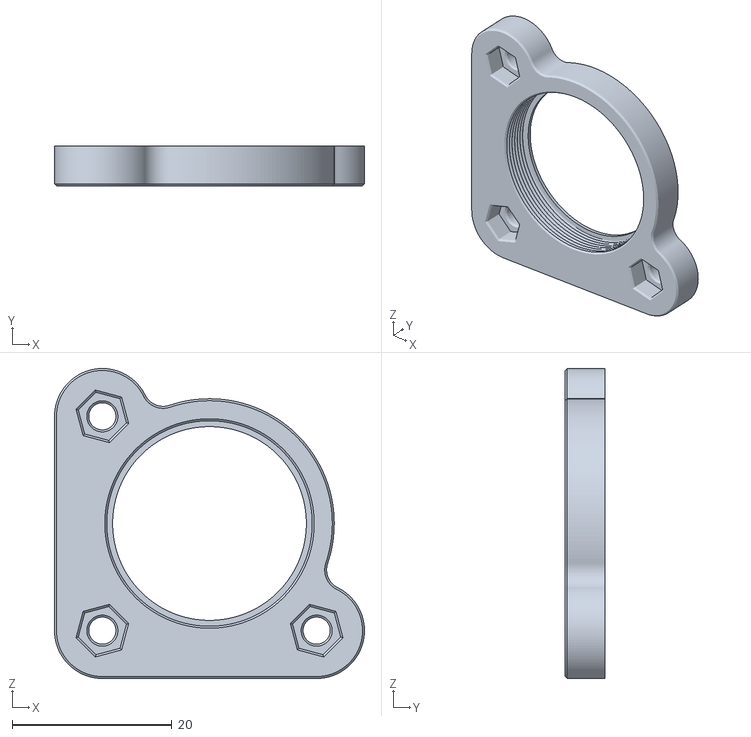
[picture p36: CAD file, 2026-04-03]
parts/Mirror-Kinematic.stl
38.9 x 5.00 x 38.9

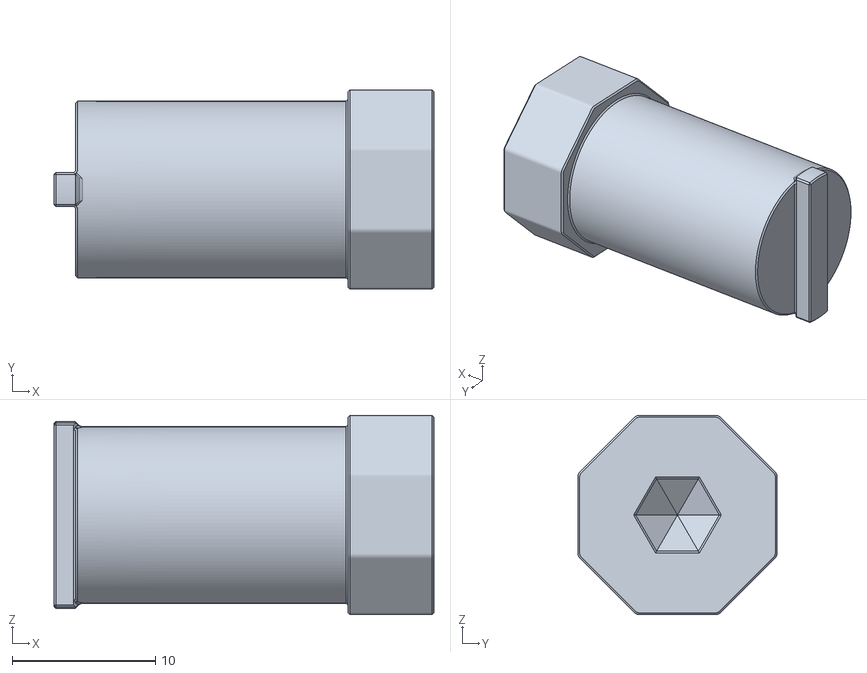
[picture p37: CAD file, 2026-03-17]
parts/Spanner_SM05RR.stl
26.5 x 13.9 x 13.9

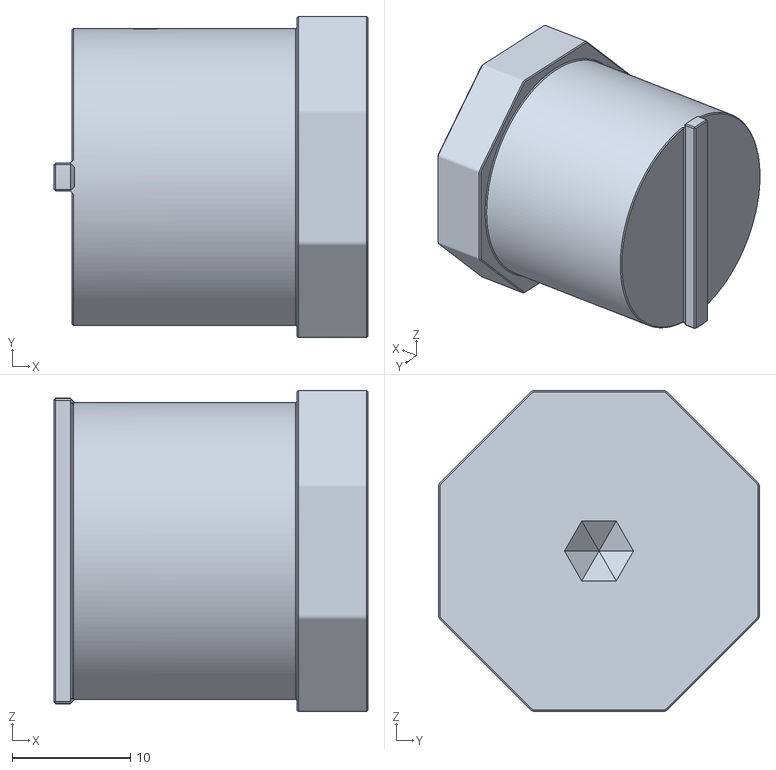
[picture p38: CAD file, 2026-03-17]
parts/Spanner_SM1RR.stl
26.5 x 27.1 x 27.1

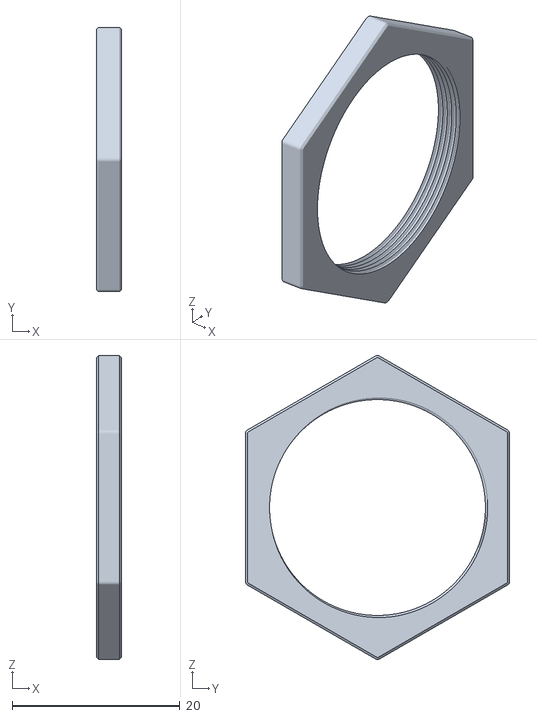
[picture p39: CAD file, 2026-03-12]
parts/SM1-Lockring.stl
3.00 x 31.6 x 36.3

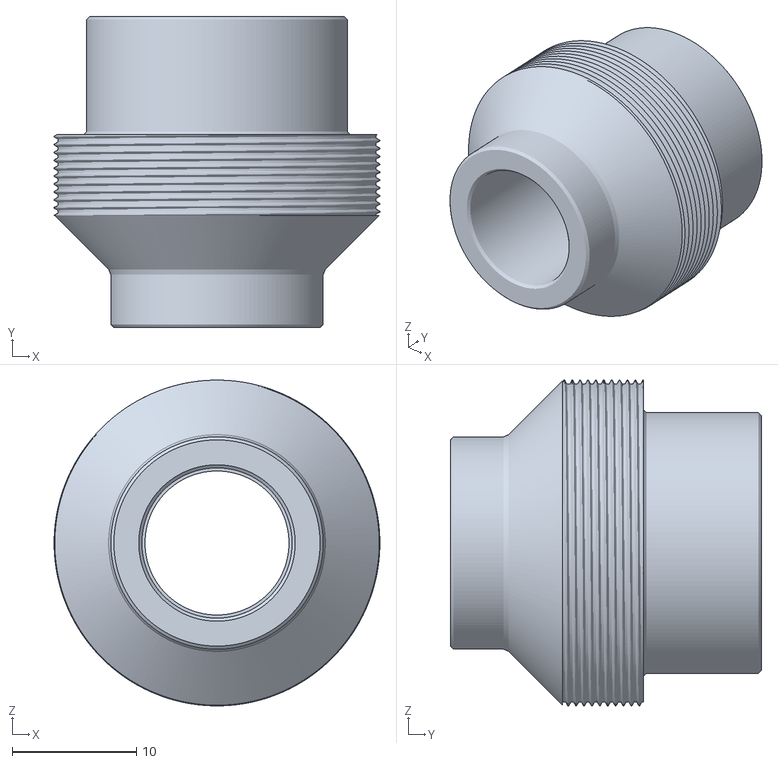
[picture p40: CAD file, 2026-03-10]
parts/Laser-Insert.stl
26.2 x 25.0 x 26.2

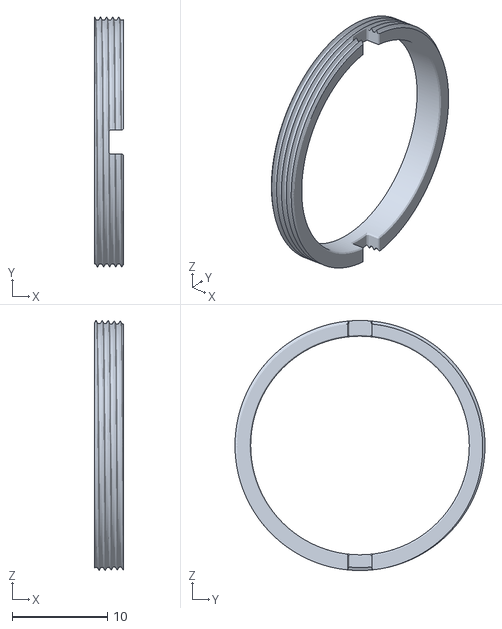
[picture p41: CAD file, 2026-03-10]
parts/SM1-RR.stl
3.01 x 26.2 x 26.2

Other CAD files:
parts/Cube-Insert_FilterFocus.stl
parts/Mirror-RR.stl
parts/SM05-RR.stl
parts/BP-RR.stl
parts/Base-Cube-Top.stl
parts/Cube-Insert_Dump.stl
parts/Dump-Aperture.stl
parts/Dump-Cone.stl

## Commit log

2026-03-10 Update - Entirely 3D-Printed Version
2026-03-10 Version 1 (Added Parts and Overview)
    [BP-RR.stl, Base-Cube-Top.stl, Base-Cube.stl, Cube-Insert_Dump.stl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]
2026-03-12 Updated formatting and part issue
    [SM1-Lockring.stl]
2026-03-17 Added Spanner & Video
    [Spanner_SM05RR.stl, Spanner_SM1RR.stl]
2026-03-19 Added more Samples
2026-04-03 Updated Parts and first Instruction Drafts
    [Base-Cube.stl, Cube-Insert_FilterFocus.stl, Cube-Insert_Laser.stl, Cube-Insert_Sample.stl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]
2026-05-04 More instructions
    [Cube-Insert_Sample_M25.stl]
